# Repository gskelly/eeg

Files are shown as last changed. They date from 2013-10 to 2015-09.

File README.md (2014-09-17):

eeg
===

Software, firmware, and CAD files for Brainboard, a mobile EEG project.
Brainboard interfaces with a custom MATLAB program, BCI2VR
(http://www.engineering.vcu.edu/eegbci/bci2vr_index.html), via Bluetooth.
The core hardware components are the ADS1299 EEG front-end from Texas
Instruments, the AT32UC3L064 microcontroller from Atmel, the MPU-6050 
6-axis inertial measurement unit from InvenSense, and the RN-42 Bluetooth
2.1 module from Microchip/Roving Networks.

Current firmware is for the Atmel AT32UC3L064, a 32-bit AVR microcontroller.
Some experimentation was done with on-line digital processing of the acquired
EEG signals from within the AVR firmware, but this is currently incomplete.
The microcontroller acts as a dumb pipe shuttling 8 channels of 24-bit data
from the ADS1299 and 6 channels of 16-bit data from the MPU-6050, where they
are displayed using the BCI2VR MATLAB GUI. Firmware is flashed to the MCU using
a 10-pin JTAG connection and the AVR Dragon (or other AVR32-compatible
programmer). Code was developed using the free Atmel Studio IDE.

The project predates my use of a proper versioning system, and thus
the hardware folder contains designs (some old, some WIP) for the Brainboard. 
***The most recent complete version is brainboard_wearable_v2.***
Older versions may be viewed for completeness's sake and/or compared with the
thesis document for a full picture of the design process.
The folders "muscleboard" and "brainboard_v2" are works in progress. The former
is meant for single-channel EMG acquisition and acceleration measurements in a
small, 3-electrode form factor that can be mounted on a disposable electrode pad.
This will probably ultimately be moved to its own repository. Brainboard v2 is a
BeagleBone Black cape that takes the BBB support from earlier versions of the
Brainboard and re-implements it in a more elegant fashion (see thesis for details).

**To use the BCI2VR GUI (assumes you already have MATLAB r2011b or later):**

1. Go to the link above and download the required MATLAB files for the basic BCI2VR functionality.

2. Copy btv_brainBoardBtFun.m into the functions folder.

3. Copy brainBoardBt_btv_daq_settings.m and brainBoardBt_14Ch.loc into the setup_files folder.

4. Make sure the toolbox is added to your path. Run bci2vr.m and click "Data Acquisition." 

5. Click the "Load setup file" icon and load brainBoardBt_btv_daq_settings.

6. The program will attempt to open a Bluetooth connection with BrainBoard. It occasionally fails; in this case simply close the GUI and try again.

7. Click the "Play" icon to begin recording.

For more info, check Dr. Ou Bai's documentation for BCI2VR, included with the toolbox.

Questions may be directed toward Graham Kelly, preferably at kellygs@vcu.edu, or at graham.smith.kelly@gmail.com as a backup. Dr. Bai may be reached at obai@vcu.edu.

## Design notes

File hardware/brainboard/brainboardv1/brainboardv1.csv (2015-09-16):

1nF | 1 | C2 | ~
2.2nF | 1 | C53 | ~
4.7nF | 11 | C20 C21 C22 C23 C24 C25 C26 C27 C28 C55 C56 | ~
0.01uF | 3 | C42 C47 C54 | ~
0.1uF | 14 | C1 C6 C11 C12 C15 C16 C17 C18 C29 C31 C33 C34 C35 C50 | ~
0.1uF | 1 | C19 | ~
0.1uF | 3 | C45 C51 C52 | ~
1uF | 7 | C4 C5 C7 C9 C10 C13 C14 | ~
1uF | 5 | C37 C38 C40 C41 C46 | ~
2.2uF | 1 | C30 | ~
2.2uF | 2 | C44 C49 | ~
10uF | 2 | C3 C32 | ~
10uF | 4 | C36 C39 C43 C48 | ~
100uF | 1 | C8 | ~
STAT | 1 | D1 | ~
CONN | 1 | D2 | ~
WP | 1 | P1 | ~
CONN_14 | 1 | P2 | ~
CONN_5X2 | 1 | P3 | ~
BTRST | 1 | P4 | ~
GND | 1 | P5 | ~
-3V3 | 1 | P6 | ~
3V3 | 1 | P7 | ~
+2V5 | 1 | P8 | ~
-2V5 | 1 | P9 | ~
CONN_2X2 | 1 | P10 | ~
330 | 2 | R24 R25 | ~
4.7K | 3 | R1 R2 R3 | ~
4.99K | 13 | R11 R12 R13 R14 R15 R16 R17 R18 R19 R20 R21 R22 R23 | ~
5.6K | 2 | R5 R6 | ~
10K | 1 | R4 | ~
10K | 3 | R7 R8 R26 | ~
499K | 0.1% | 1 | R9 | ~
SMT_BUTTON | 1 | S2
NO BIAS FILT | 1 | SJ3 | SparkFun-Passives-SJ_2S-NO
A2 | 1 | SJ4 | SparkFun-Passives-SJ_2S-NOTRACE
A1 | 1 | SJ5 | SparkFun-Passives-SJ_2S-NOTRACE
CLKSEL | 1 | SJ8 | SparkFun-Passives-SJ_3_PASTE1&2
REF-SRB2 | 1 | SJ1 | SparkFun-Passives-SJ_3_PASTE2&3
DAISY_CS | 2 | SJ2 SJ7 | SparkFun-Passives-SJ_3_PASTE2&3
DAISY_OUT | 1 | SJ6 | SparkFun-Passives-SJ_3_PASTE2&3
I2C Address Select (2&3NC) | 1 | SJ9 | SparkFun-Passives-SJ_3_PASTE2&3
24C256 | 1 | U1
BEAGLEBONE_BLACK | 1 | U2
ATUC3L064 | 1 | U8
BLUETOOTH-RN42 | 1 | U9
MPU6050 | 1 | U13
OPA2376 | 1 | U3 | MSOP8
ADS1299 | 1 | U4 | TQFP_64
TPD4E001DBV | 3 | U5 U6 U7 | ~
TPS60403 | 1 | U10 | ~
TPS73225 | 1 | U11 | ~
TPS72325 | 1 | U12 | ~

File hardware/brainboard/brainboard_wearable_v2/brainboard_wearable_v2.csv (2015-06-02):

1nF | 1 | C7
2.2nF | 1 | C3
4.7nF | 11 | C53 C54 C55 C56 C57 C58 C59 C60 C61 C62 C63
0.01uF | 4 | C4 C33 C34 C35
0.1uF | 5 | C1 C2 C24 C31 C42
0.1uF | 15 | C5 C6 C11 C15 C18 C19 C22 C23 C43 C45 C47 C48 C49 C50 C51
0.1uF | 1 | C52
1uF | 8 | C9 C10 C12 C14 C16 C17 C20 C21
1uF | 4 | C27 C28 C30 C32
2.2uF | 4 | C25 C39 C40 C41
2.2uF | 1 | C44
10uF | 2 | C8 C46
10uF | 5 | C26 C29 C36 C37 C38
100uF | 1 | C13
USB | 1 | CON1
SMAJ7.0A | 1 | D1
BATTLO | 1 | D2
PGOOD | 1 | D3
CHARGE | 1 | D4
STAT | 1 | D5
CONN | 1 | D6
PTC 500mA | 1 | F1
MHOLE | 3 | MTG1 MTG2 MTG3
JST | 1 | P1
CONN_5X2 | 1 | P8
CONN_14 | 1 | P10
1.18k | 1 | R13
2.2k | 4 | R11 R14 R15 R16
2.2k | 2 | R17 R18
4.7k | 2 | R4 R5
4.99K | 12 | R21 R22 R23 R24 R25 R26 R27 R28 R29 R30 R31 R32
10K | 2 | R1 R2
10k | 4 | R6 R7 R19 R20
51.1k | 1 | R9
52.3k | 1 | R12
383k | 1 | R10
499K 0.10% | 1 | R3
562k | 1 | R8
DPDT | 1 | S1
NO BIAS FILT | 1 | SJ1
NTC 10K | 1 | TH1
GND | 2 | TP1 TP2
PREREG | 1 | TP3
-3V3 | 1 | TP4
+2V5 | 1 | TP5
-2V5 | 1 | TP6
BTRST | 1 | TP7
3V3 | 1 | TP8
MPU6050 | 1 | U1
LTC1998 | 1 | U4
BQ24074(T) | 1 | U5
ATUC3L064 | 1 | U10
BLUETOOTH-RN42 | 1 | U11
OPA2376 | 1 | U2
ADS1299 | 1 | U3
TPS60403 | 1 | U6
TPS73233 | 1 | U7
TPS73225 | 1 | U8
TPS72325 | 1 | U9
TPD4E001DBV | 3 | U12 U13 U14

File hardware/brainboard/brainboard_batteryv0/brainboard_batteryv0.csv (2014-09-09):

0.01uF | 2 | C6 C8 | ~
0.1uF | 2 | C1 C11 | ~
0.47uF | 1 | C9 | ~
2.2uF | 1 | C10 | ~
10uF | 5 | C2 C3 C4 C5 C7 | ~
USB-MINI-B | 1 | CON1 | ~
SMAJ7.0A | 1 | D1 | ~
PGOOD | 1 | D2 | ~
CHARGE | 1 | D3 | ~
PMEG2005AEA | 1 | D4 | ~
POWER | 1 | D5 | ~
ALRT | 1 | D6 | ~
PTC 1.95A | 2 | F1 F2 | ~
JST | 1 | P1 | ~
VBAT | 1 | P2 | ~
GND | 1 | P3 | ~
BBB_PMIC | 1 | P4 | ~
VBUS | 1 | P6 | ~
WP | 1 | P7 | ~
EN | 1 | P8 | ~
PREREG | 1 | P9 | ~
3V3 | 1 | P10 | ~
SI2312 | 1 | Q1 | ~
1.18k | 1 | R7 | ~
2.2k | 5 | R8 R10 R11 R18 R19 | ~
4.7k | 3 | R2 R3 R4 | ~
5.6k | 2 | R12 R13 | ~
10k | 1 | R9 | ~
30.1k | 1 | R14 | ~
52.3k | 2 | R15 R16 | ~
75k | 1 | R1 | ~
191k | 1 | R6 | ~
806k | 2 | R5 R17 | ~
SYSOFF | 1 | S1 | ~
BBB_SLEEP | 1 | S2 | ~
TS PMIC | 1 | SJ3 | SparkFun-Passives-SJ_2S
BAT | 2 | SJ1 SJ2 | SparkFun-Passives-SJ_2S-NO
A2-0 | 1 | SJ4 | SparkFun-Passives-SJ_2S-NO
A1-0 | 1 | SJ5 | SparkFun-Passives-SJ_2S-NO
SENSE | 1 | SJ7 | SparkFun-Passives-SJ_2S-NO
LOWBAT_DIS | 1 | SJ6 | SparkFun-Passives-SJ_3_PASTE1&2
NTC 10K | 1 | TH1 | ~
MAX17048 | 1 | U1
BQ24074(T) | 1 | U2
24C256 | 1 | U3 | ~
TPS73601-SON | 1 | U4 | ~
LTC2951-1 | 1 | U5 | ~
BEAGLEBONE_BLACK | 1 | U6 | ~

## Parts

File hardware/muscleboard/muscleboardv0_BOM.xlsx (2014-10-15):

Item Value | Count | Reference | Manufacturer | Distributor | PN | Description | Note
1.5nF | 1 | C19 |  | Digi-Key | 04025C152JAT2A | CAP CER 1500PF 50V 5% X7R 0402
4.7nF | 2 | C13 C14 |  | Digi-Key | CL05B472KB5NNNC | CAP CER 4700PF 50V 10% X7R 0402
0.01uF | 1 | C10 |  | Digi-Key | C0402C103K4RACTU | CAP CER 10000PF 16V 10% X7R 0402 | Need to order
0.1uF | 10 | C1 C2 C3 C5 C15 C20 C21 C9 C23 C25 |  | Digi-Key | CL05A104MP5NNNC | CAP CER 0.1UF 10V 20% X5R 0402
1uF | 4 | C17 C18 C22 C24 |  | Digi-Key | JMK105BJ105KV-F | CAP CER 1UF 6.3V 10% X5R 0402
2.2uF | 1 | C12 |  | Digi-Key | C0402C225M9PACTU | CAP CER 2.2UF 6.3V 20% X5R 0402 | Need to order
4.7uF | 2 | C4 C8 |  | Digi-Key | GRM155R60J475ME47D | CAP CER 4.7UF 6.3V 20% X5R 0402 | Need to order
10uF | 2 | C11 C16 |  | Digi-Key | CL10A106MQ8NNNC | CAP CER 10UF 6.3V 20% X5R 0603
CHG | 1 | D1 |  | Digi-Key | APT1608SGC | LED 1.6X0.8MM 568NM GRN CLR SMD
SCHOTTKY | 1 | D2 |  | Digi-Key | VS-10BQ015-M3/5BT | DIODE SCHOTTKY 15V 1A SMB
RED | 1 | D3 |  | Digi-Key | APT1608SRCPRV | LED 1.6X0.8MM 640NM RED CLR SMD
BLM18PG121SN1 | 1 | FB1 |  | Digi-Key | BLM18PG121SN1D | FERRITE CHIP 120 OHM 2000MA 0603
10uH | 1 | L1 |  | Digi-Key | MLZ1608E100M | INDUCTOR MULTILAYER 10UH 0603
BATT | 1 | P1 |  | Digi-Key | S2B-PH-SM4-TB(LF)(SN) | CONN HEADER PH SIDE 2POS 2MM SMD
USB | 1 | P2 |  | Digi-Key | 690-005-299-043 | CONN MINI USB RCPT RA TYPE B SMD
ICSP | 1 | P3 |  | Digi-Key | 67996-206HLF | CONN HEADER 6POS .100 STR 15AU
2.2k | 2 | R4 R7 |  | Digi-Key | RMCF0402FT2K20 | RES 2.2K OHM 1/16W 1% 0402
10k | 4 | R3 R5 R9 R10 |  | Digi-Key | RMCF0402JT10K0 | RES 10K OHM 1/16W 5% 0402
51k | 1 | R8 |  | Digi-Key | RMCF0402FT51K0 | RES 51K OHM 1/16W 1% 0402
1M | 2 | R2 R12 |  | Digi-Key | RMCF0402JT1M00 | RES 1M OHM 1/16W 5% 0402
2.2M | 1 | R1 |  | Digi-Key | RC1005F225CS | RES 2.2M OHM 1/16W 1% 0402
CHG/ON | 1 | S2 |  | Digi-Key | JS102011SAQN | SWITCH SLIDE 1PDT 6VDC 0.3A SMT
ADS1291 | 1 | U5 |  | Digi-Key | ADS1291IRSMT | IC AFE 24BIT 8KSPS 1CH 32VQFN | Need to order
ATMEGA328P | 1 | U1 |  | Digi-Key | ATMEGA328P-MUR | IC MCU 8BIT 32KB FLASH 32QFN | Need to order
MCP73831T-DFN | 1 | U2 |  | Mouser | MCP73831T-2ACI/MC | Battery Management Charge mgnt contr | Need to order
TPS73233 | 1 | U3 |  | Digi-Key | TPS73233DBVT | IC REG LDO 3.3V 0.25A SOT23-5
BLUETOOTH-RN42 | 1 | U4 |  | Digi-Key | RN42-I/RM | MODULE BLUETOOTH V2.1+EDR | Need to order
ADXL362 | 1 | U6 |  | Digi-Key | ADXL362BCCZ-RL7 | IC ACCEL DIG LO PWR 3AX 16LGA | Need to order
RESONATOR | 1 | Y1 |  | Digi-Key | CSTCE8M00G52-R0 | CER RESONATOR

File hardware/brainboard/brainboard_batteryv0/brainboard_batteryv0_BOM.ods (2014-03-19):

VALUE | REF | COUNT | DESCRIPTION/COMMENTS | VENDOR | PN
0.01uF | C6 C8 | 2 | SM0603 | DigiKey | 1276-1926-1-ND
0.1uF | C1 | 1 | SM0603 | DigiKey | 1276-1258-1-ND
0.47uF | C9 | 1 | SM0603 | DigiKey | 1276-2378-1-ND
2.2uF | C10 | 1 | SM0603 | DigiKey | 1276-1040-1-ND
10uF | C2 C3 C7 | 3 | SM0805 | DigiKey | 1276-2893-1-ND
10uF | C4 C5 | 2 | SM1206 | DigiKey | 1276-2876-1-ND
USB-MINI-B | CON1 | 1 | SMD W/ BOARD GUIDE | DigiKey | 151-1206-1-ND
SMAJ7.0A | D1 | 1 | ZENER | DigiKey | SMAJ7.0ALFCT-ND
PGOOD | D2 | 1 | LED | DigiKey | -
CHARGE | D3 | 1 | LED | DigiKey | -
PMEG2005AEA | D4 | 1 | SCHOTTKY | DigiKey | 568-6498-1-ND
PTC 1.95A | F1 F2 | 2 | LITTELFUSE 1812L | DigiKey | F3485CT-ND
JST | P1 | 1 | JST FEM PH 2PIN SMD | DigiKey | 455-1749-1-ND
VBAT | P2 | 1 | TP | - | -
GND | P3 | 1 | TP | - | -
BBB_PMIC | P4 | 1 | 2X2 MALE
~ALRT | P5 | 1 | TP | - | -
VBUS | P6 | 1 | TP | - | -
WP | P7 | 1 | TP | - | -
EN | P8 | 1 | TP | - | -
PREREG | P9 | 1 | TP | - | -
3V3 | P10 | 1 | TP | - | -
SI2312 | Q1 | 1 | NMOS | DigiKey | SI2312CDS-T1-GE3CT-ND
1.18k | R7 | 1 | 1% | DigiKey | 311-1.18KHRCT-ND
1.5k | R10 R11 | 2 |  | DigiKey | 311-1.5KGRCT-ND
2.2k | R8 | 1 | 1% | DigiKey | 311-2.20KHRCT-ND
4.7k | R2 R3 R4 | 3 |  | DigiKey | 311-4.7KGRCT-ND
5.6k | R12 R13 | 2 |  | DigiKey | 311-5.6KGRCT-ND
10k | R9 | 1 |  | DigiKey | 311-10KGRCT-ND
30.1k | R14 | 1 | 1% | DigiKey | 311-30.1KHRCT-ND
52.3k | R15 R16 | 2 | 1% | DigiKey | 311-52.3KHRCT-ND
75k | R1 | 1 | 1% | DigiKey | 311-75.0KHRCT-ND
191k | R6 | 1 | 1% | DigiKey | 311-191KHRCT-ND
806k | R5 R17 | 2 | 1% | DigiKey | 311-806KHRCT-ND
SYSOFF | S1 | 1 | MOM BUTTON | DigiKey | -
BBB_SLEEP | S2 | 1 | MOM BUTTON | DigiKey | -
TO PMIC | SJ3 | 1 | SOLDER JUMPER | - | -
BAT | SJ1 SJ2 | 2 | SOLDER JUMPER | - | -
A2-0 | SJ4 | 1 | SOLDER JUMPER | - | -
A1-0 | SJ5 | 1 | SOLDER JUMPER | - | -
LOWBAT_DIS | SJ6 | 1 | SOLDER JUMPER | - | -
NTC 10K | TH1 | 1 | SM0402 | DigiKey | BC2329CT-ND
MAX17048 | U1 | 1 | FUEL GAUGE | Mouser | 700-MAX17048G+
BQ24074(T) | U2 | 1 | CHARGER | DigiKey | 296-23798-1-ND
24C256 | U3 | 1 | EEPROM | DigiKey | -
TPS73601-SON | U4 | 1 | LDO | DigiKey | 296-27062-1-ND
LTC2951-1 | U5 | 1 | ON/OFF CTRL IC | DigiKey | LTC2951CDDB-1#TRMPBFCT-ND
BEAGLEBONE_BLACK | U6 | 1 | CAPE FOOTPRINT | - | -

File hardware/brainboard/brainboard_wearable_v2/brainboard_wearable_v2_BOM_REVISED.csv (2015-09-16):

VALUE | COUNT | REF
1nF | 1 | C7 | ~ | Kemet | C0603C102K3RACTU | DigiKey | $0.10/1 $0.02/10 $0.0108/50
2.2nF | 1 | C3 | ~
4.7nF | 11 | C53 C54 C55 C56 C57 C58 C59 C60 C61 C62 C63 | ~ | Kemet | C0603C472K5RACTU | DigiKey | $0.10/1 $0.03/10 $0.0162/50
0.01uF | 4 | C4 C33 C34 C35 | ~
0.1uF | 5 | C1 C2 C24 C31 C42 | ~
0.1uF | 15 | C5 C6 C11 C15 C18 C19 C22 C23 C43 C45 C47 C48 C49 C50 C51 | ~ | Kemet | C0603C104K4RACTU | DigiKey | $0.10/1 $0.022/10 $0.0118/50
0.1uF | 1 | C52 | ~ | Kemet | C0603C104K4RACTU | DigiKey | $0.10/1 | $0.022/10 | $0.0118/50
1uF | 8 | C9 C10 C12 C14 C16 C17 C20 C21 | ~ | Kemet | C0603C105K8PACTU | DigiKey | $0.10/1 $0.039/10 $0.021/50
1uF | 4 | C27 C28 C30 C32 | ~
2.2uF | 4 | C25 C39 C40 C41 | ~
2.2uF | 1 | C44 | ~ | Kemet | C0603C225K8PACTU | DigiKey | $0.17/1 $0.113/10 $0.0676/50
10uF | 2 | C8 C46 | ~ | Kemet | C0805C106Z8VACTU | DigiKey | $0.16/1 $0.111/10 $0.063/50
10uF | 5 | C26 C29 C36 C37 C38 | ~
100uF | 1 | C13 | ~ | Vishay Sprague | TL8A0107M010C | DigiKey | $1.35/1 $1.128/10
USB | 1 | CON1 | ~
SMAJ7.0A | 1 | D1 | ~
BATTLO | 1 | D2 | ~
PGOOD | 1 | D3 | ~
CHARGE | 1 | D4 | ~
STAT | 1 | D5 | ~ | Kingbright Company LLC | APT1608SRCPRV | DigiKey | $0.17/1 $0.131/10 $0.1044/25
CONN | 1 | D6 | ~ | Kingbright Company LLC | APT1608SGC | DigiKey | $0.16/1 $0.117/10 $0.0936/25
PTC 500mA | 1 | F1 | ~
MHOLE | 3 | MTG1 MTG2 MTG3 | ~
JST | 1 | P1 | ~
CONN_5X2 | 1 | P8 | ~ | FCI | 95278-101B10LF | Mouser | $0.86/1 $0.737/10 $0.673/100
CONN_14 | 1 | P10 | ~
1.18k | 1 | R13 | ~
2.2k | 4 | R11 R14 R15 R16 | ~
2.2k | 2 | R17 R18 | ~ | Stackpole Electronics | RMCF0603JT330R | DigiKey | $0.02/1 $0.017/10 $0.0092/50
4.7k | 2 | R4 R5 | ~
4.99K | 12 | R21 R22 R23 R24 R25 R26 R27 R28 R29 R30 R31 R32 | ~ | Stackpole Electronics | RNCS0603BKE4K99 | DigiKey | $0.70/1 $0.475/10 $0.2876/50
10K | 2 | R1 R2 | ~ | Stackpole Electronics | RMCF0603JT10K0 | DigiKey | $0.02/1 $0.017/10 $0.0092/50
10k | 4 | R6 R7 R19 R20 | ~
51.1k | 1 | R9 | ~
52.3k | 1 | R12 | ~
383k | 1 | R10 | ~
499K 0.10% | 1 | R3 | ~ | Stackpole Electronics | RNCS0805BKE499K | DigiKey | $0.77/1 | $0.523/10 | $0.3162/50
562k | 1 | R8 | ~
DPDT | 1 | S1 | ~
NO BIAS FILT | 1 | SJ1 | SparkFun-Passives-SJ_2S-NO
NTC 10K | 1 | TH1 | ~
GND | 2 | TP1 TP2 | ~
PREREG | 1 | TP3 | ~
-3V3 | 1 | TP4 | ~
+2V5 | 1 | TP5 | ~
-2V5 | 1 | TP6 | ~
BTRST | 1 | TP7 | ~
3V3 | 1 | TP8 | ~
MPU6050 | 1 | U1
LTC1998 | 1 | U4
BQ24074(T) | 1 | U5
ATUC3L064 | 1 | U10 |  | Atmel | AT32UC3L064-AUT | DigiKey | $7.80/1 $4.898/25
BLUETOOTH-RN42 | 1 | U11 |  | Microchip Technology | RN42-I/RM | DigiKey | $19.14/1 $15.95/10
OPA2376 | 1 | U2 | MSOP8 | Texas Instruments | OPA2376AIDGKR | DigiKey | $2.73/1 $2.462/10 $2.206/25
ADS1299 | 1 | U3 | TQFP_64 | Texas Instruments | ADS1299IPAG | DigiKey | $58.14/1
TPS60403 | 1 | U6 | ~
TPS73233 | 1 | U7 | ~
TPS73225 | 1 | U8 | ~
TPS72325 | 1 | U9 | ~
TPD4E001DBV | 3 | U12 U13 U14 | ~

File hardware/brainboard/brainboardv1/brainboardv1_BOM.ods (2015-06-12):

VALUE | REF | COUNT | DESCRIPTION/COMMENTS | VENDOR | PN | Price Breaks
1nF | C36 | 1 | Kemet Ceramic | DigiKey | C0603C102K3RACTU | $0.10/1 $0.02/10 $0.0108/50
2.2nF | C53 | 1 | Samsung Electro-Mechanics | DigiKey | CL10A225KO8NNNC
4.7nF | C4 C5 C6 C7 C8 C9 C10 C11 C12 | 9 | Kemet | DigiKey | C0603C472K5RACTU | $0.10/1 $0.03/10 $0.0162/50
0.01uF | C27 C28 C54 | 3 | Kemet | DigiKey | C0603C103K5RACTU
0.1uF | C1 C2 C3 C13 C15 C17 C18 C19 C33 C34 C35 C40 C45 C46 C49 C50 C51 C52 | 18 | Kemet | DigiKey | C0603C104K4RACTU | $0.10/1 $0.022/10 $0.0118/50
1uF | C21 C22 C24 C25 C26 C38 C39 C41 C43 C44 C47 C48 | 12 | Kemet | DigiKey | C0603C105K8PACTU | $0.10/1 $0.039/10 $0.021/50
2.2uF | C14 C31 C32 | 3 | Kemet | DigiKey | C0603C225K8PACTU
10uF | C16 C20 C23 C29 C30 C37 | 6 | Kemet | DigiKey | C0805C106Z8VACTU | $0.16/1 $0.111/10 $0.063/50
100uF | C42 | 1 | Vishay Sprague Tant Pol | DigiKey | TL8A0107M010C | $1.35/1 $1.128/10
RED | D1 | 1 | Kingbright Company LLC | DigiKey | APT1608SRCPRV | $0.17/1 $0.131/10 $0.1044/25
GREEN | D2 | 1 | Kingbright Company LLC | DigiKey | APT1608SGC | $0.16/1 $0.117/10 $0.0936/25
CONN_14 | P2 | 1 | Sullins Connector | DigiKey | PPTC141LGBN-RC
CONN_5X2 | P3 | 1 | FCI | DigiKey | 68602-110HLF | $0.33/1 $0.308/10 $0.2644/25
330 | R20 R21 | 2 | Stackpole Electronics | DigiKey | RMCF0603JT330R | $0.02/1 $0.017/10 $0.0092/50
4.7K | R1 R2 R3 | 3 | Stackpole Electronics | DigiKey | RMCF0603JT4K70 | $0.02/1 $0.017/10 $0.0092/50
4.99K | R7 R8 R9 R10 R11 R12 R13 R14 R15 R16 R17 R18 R19 | 13 | Stackpole Electronics | DigiKey | RNCS0603BKE4K99 | $0.70/1 $0.475/10 $0.2876/50
5.6K | R5 R6 | 2 | Stackpole Electronics | DigiKey | RMCF0603JT5K60 | $0.02/1 $0.017/10 $0.0092/50
10K | R4 | 1 | Stackpole Electronics | DigiKey | RMCF0603JT10K0 | $0.02/1 $0.017/10 $0.0092/50
10K | R22 R23 R24 R26 R27 | 5 | Stackpole Electronics | DigiKey | RMCF0603JT10K0 | $0.02/1 $0.017/10 $0.0092/50
499K 0.10% | R25 | 1 | Stackpole Electronics | DigiKey | RNCS0805BKE499K | $0.77/1 $0.523/10 $0.3162/50
SMT_BUTTON | S2 | 1 | C&K Components | DigiKey | KMR231GLFS | $0.64/1 $0.604/10 $0.5436/25
24C256 | U1 | 1 | Fremont Micro Devices USA | DigiKey | FT24C256A-UMR-B | $0.92/1 $0.805/10 $0.7132/25
BEAGLEBONE_BLACK | U2 | 1
ATUC3L064 | U6 | 1 | Atmel | DigiKey | AT32UC3L064-AUT | $7.80/1 $4.898/25
BLUETOOTH-RN42 | U7 | 1 | Microchip Technology | DigiKey | RN42-I/RM | $19.14/1 $15.95/10
MPU6050 | U13 | 1 | InvenSense | DigiKey | 1428-1007-1-ND
OPA2376 | U11 | 1 | Texas Instruments | DigiKey | OPA2376AIDGKR | $2.73/1 $2.462/10 $2.206/25
ADS1299 | U12 | 1 | Texas Instruments | DigiKey | ADS1299IPAG | $58.14/1
TPD4E001DBV | U3 U4 U5 | 3 | Texas Instruments | DigiKey | 296-28203-1-ND
TPS60403 | U8 | 1 | Texas Instruments | DigiKey | 296-13418-1-ND
TPS73225 | U9 | 1 | Texas Instruments | DigiKey | 296-15810-1-ND
TPS72325 | U10 | 1 | Texas Instruments | DigiKey | 296-15799-1-ND

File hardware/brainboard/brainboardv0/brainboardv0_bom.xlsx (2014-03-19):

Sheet: Order Request Form
Item | Vendor | PN | Count/Bd | Count/Run | Order | Unit Price | Subtotal
RES 330 OHM 1/10W 5% 0603 | DigiKey | RMCF0603JT330R | 2 | 6 | 10 | $0.0170 | $0.17
CAP CER 0.1UF 16V 10% X7R 0603 | DigiKey | C0603C104K4RACTU | 15 | 45 | 50 | $0.0118 | $0.59
CAP TANT 100UF 10V 20% 1206 | DigiKey | TL8A0107M010C | 1 | 3 | 10 | $1.1280 | $11.28
RES 10K OHM 1/10W 5% 0603 | DigiKey | RMCF0603JT10K0 | 5 | 15 | 20 | $0.0170 | $0.34
CAP CER 10UF 10V Y5V 0805 | DigiKey | C0805C106Z8VACTU | 2 | 6 | 20 | $0.1110 | $2.22
CAP CER 1000PF 25V 10% X7R 0603 | DigiKey | C0603C102K3RACTU | 1 | 3 | 10 | $0.0200 | $0.20
CAP CER 1UF 10V 10% X5R 0603 | DigiKey | C0603C105K8PACTU | 7 | 21 | 50 | $0.0210 | $1.05
CAP CER 2.2UF 10V 10% X5R 0603 | DigiKey | C0603C225K8PACTU | 1 | 3 | 10 | $0.1130 | $1.13
CAP CER 4700PF 50V 10% X7R 0603 | DigiKey | C0603C472K5RACTU | 9 | 27 | 50 | $0.0162 | $0.81
RES 4.7K OHM 1/10W 5% 0603 | DigiKey | RMCF0603JT4K70 | 3 | 9 | 20 | $0.0170 | $0.34
RES 4.99K OHM 1/16W 0.1% 0603 | DigiKey | RNCS0603BKE4K99 | 11 | 33 | 50 | $0.2876 | $14.38
RES 5.6K OHM 1/10W 5% 0603 | DigiKey | RMCF0603JT5K60 | 2 | 6 | 20 | $0.0170 | $0.34
RES 499K OHM 1/10W 0.1% 0805 | DigiKey | RNCS0805BKE499K | 1 | 3 | 10 | $0.5230 | $5.23
LED 1.6X0.8MM 568NM GRN CLR SMD | DigiKey | APT1608SGC | 1 | 3 | 10 | $0.1170 | $1.17
LED 1.6X0.8MM 640NM RED CLR SMD | DigiKey | APT1608SRCPRV | 1 | 3 | 10 | $0.1310 | $1.31
SWITCH TACTILE SPST-NO 0.05A 32V | DigiKey | KMR231GLFS | 1 | 3 | 10 | $0.6040 | $6.04
CONN FEMALE 12POS .100" R/A GOLD | DigiKey | PPPC121LGBN-RC | 1 | 3 | 10 | $0.8400 | $8.40
BERGSTIK II .100" DR STRAIGHT | DigiKey | 68602-110HLF | 1 | 3 | 10 | $0.6710 | $6.71
IC EEPROM 256KBIT 1MHZ 8MSOP | DigiKey | FT24C256A-UMR-B | 1 | 3 | 5 | $0.9200 | $4.60
IC AFE 24BIT 16KSPS LN 64TQFP | DigiKey | ADS1299IPAG | 1 | 3 | 3 | $58.1400 | $174.42
IC MCU 32BIT 64KB FLASH 48TQFP | DigiKey | AT32UC3L064-AUT | 1 | 3 | 3 | $7.8000 | $23.40
MODULE BLUETOOTH V2.1+EDR | DigiKey | RN42-I/RM | 1 | 3 | 3 | $19.1400 | $57.42
IC OPAMP GP 5.5MHZ DUAL 8VSSOP | DigiKey | OPA2376AIDGKR | 1 | 3 | 5 | $2.7300 | $13.65
Low-Cap 4Ch +/-15kV ESD Protection Array | Mouser | 595-TPD4E001DBVR | 3 | 9 | 10 | $0.3600 | $3.60
IC REG LDO 5V 0.15A SOT23-5 | DigiKey | TPS73150DBVT | 1 | 3 | 5 | $1.2300 | $6.15
Stacking Header Set for Beagle Bone Capes (2x23) | Adafruit | 706 | 1 | 3 | 3 | $4.9500 | $14.85
 |  | BD/RUN: | 3 |  | PARTS TOTAL/RUN: |  | $359.80
 |  | COST/BD: | $25.00 |  | PARTS TOTAL/BD: |  | $119.93
 |  | BD TOTAL/RUN: | $75.00
 |  |  |  |  | GRAND TOTAL/RUN: |  | $434.80
 |  |  |  |  | GRAND TOTAL/BD: |  | $144.93

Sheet: Price Breaks
Price Break | RMCF0603JT330R | C0603C104K4RACTU | TL8A0107M010C | RMCF0603JT10K0 | C0805C106Z8VACTU | C0603C102K3RACTU | C0603C105K8PACTU | C0603C225K8PACTU | C0603C472K5RACTU | RMCF0603JT4K70 | RNCS0603BKE4K99 | RMCF0603JT5K60 | RNCS0805BKE499K | APT1608SGC | APT1608SRCPRV | KMR231GLFS | PPPC121LGBN-RC | 68602-110HLF | FT24C256A-UMR-B | ADS1299IPAG | AT32UC3L064-AUT | RN42-I/RM | OPA2376AIDGKR | 595-TPD4E001DBVR | TPS73150DBVT | 706
0 | $0.00 | $0.00 | $0.00 | $0.00 | $0.00 | $0.00 | $0.00 | $0.00 | $0.00 | $0.00 | $0.00 | $0.00 | $0.00 | $0.00 | $0.00 | $0.00 | $0.00 | $0.00 | $0.00 | $0.00 | $0.00 | $0.00 | $0.00 | $0.00 | $0.00 | $0.00
1 | $0.020000 | $0.100000 | $1.350000 | $0.020000 | $0.160000 | $0.100000 | $0.100000 | $0.170000 | $0.100000 | $0.020000 | $0.700000 | $0.020000 | $0.770000 | $0.160000 | $0.170000 | $0.640000 | $1.010000 | $0.710000 | $0.920000 | $58.140000 | $7.800000 | $19.140000 | $2.730000 | $0.480000 | $1.230000 | $4.950000
10 | $0.017000 | $0.022000 | $1.128000 | $0.017000 | $0.111000 | $0.020000 | $0.039000 | $0.113000 | $0.030000 | $0.017000 | $0.475000 | $0.017000 | $0.523000 | $0.117000 | $0.131000 | $0.604000 | $0.840000 | $0.671000 | $0.805000 | $54.720000 | $7.800000 | $15.950000 | $2.462000 | $0.360000 | $1.091000 | $4.460000
25 | $0.017000 | $0.022000 | $1.128000 | $0.017000 | $0.111000 | $0.020000 | $0.039000 | $0.113000 | $0.030000 | $0.017000 | $0.475000 | $0.017000 | $0.523000 | $0.117000 | $0.131000 | $0.543600 | $0.777600 | $0.575200 | $0.713200 | $54.720000 | $4.898000 | $15.437600 | $2.206000 | $0.360000 | $0.984800 | $4.460000
50 | $0.009200 | $0.011800 | $1.128000 | $0.009200 | $0.063000 | $0.010800 | $0.021000 | $0.067600 | $0.016200 | $0.009200 | $0.287600 | $0.009200 | $0.316200 | $0.093600 | $0.104400 | $0.483200 | $0.699800 | $0.488800 | $0.621000 | $54.720000 | $4.898000 | $15.437600 | $2.206000 | $0.360000 | $0.984800 | $4.460000
100 | $0.007000 | $0.009900 | $0.828000 | $0.007000 | $0.052200 | $0.008800 | $0.017200 | $0.057000 | $0.013800 | $0.007000 | $0.237500 | $0.007000 | $0.261300 | $0.084500 | $0.094300 | $0.463000 | $0.622000 | $0.488800 | $0.540520 | $46.170000 | $4.353600 | $15.437600 | $1.154300 | $0.190000 | $0.461700 | $3.960000
250 | $0.005200 | $0.008120 | $0.720000 | $0.005200 | $0.043200 | $0.007400 | $0.014360 | $0.046520 | $0.011240 | $0.005200 | $0.187520 | $0.005200 | $0.206240 | $0.078000 | $0.087000 | $0.422720 | $0.544240 | $0.488800 | $0.460000 | $45.315000 | $4.353600 | $15.437600 | $1.132880 | $0.190000 | $0.461700 | $3.960000
500 | $0.003840 | $0.006940 | $0.672000 | $0.003840 | $0.036600 | $0.006300 | $0.012260 | $0.039000 | $0.009620 | $0.003840 | $0.160000 | $0.003840 | $0.176000 | $0.070200 | $0.078300 | $0.402600 | $0.497600 | $0.488800 | $0.402510 | $44.460000 | $4.353600 | $15.437600 | $1.111500 | $0.190000 | $0.461700 | $3.960000
750 | $0.003840 | $0.006940 | $0.672000 | $0.003840 | $0.036600 | $0.006300 | $0.012260 | $0.039000 | $0.009620 | $0.003840 | $0.160000 | $0.003840 | $0.176000 | $0.070200 | $0.078300 | $0.402600 | $0.497600 | $0.488800 | $0.402510 | $43.605000 | $4.353600 | $15.437600 | $1.109012 | $0.190000 | $0.461700 | $3.960000
1000 | $0.002560 | $0.005400 | $0.528000 | $0.002560 | $0.036600 | $0.004950 | $0.009630 | $0.034500 | $0.007500 | $0.002560 | $0.160000 | $0.002560 | $0.176000 | $0.070200 | $0.078300 | $0.332150 | $0.450950 | $0.488800 | $0.368000 | $42.750000 | $4.353600 | $15.437600 | $1.109012 | $0.170000 | $0.461700 | $3.960000
2500 | $0.002160 | $0.005400 | $0.528000 | $0.002160 | $0.036600 | $0.004950 | $0.009630 | $0.034500 | $0.007500 | $0.002160 | $0.160000 | $0.002160 | $0.176000 | $0.070200 | $0.078300 | $0.332150 | $0.404300 | $0.488800 | $0.333500 | $42.750000 | $4.353600 | $15.437600 | $1.109012 | $0.170000 | $0.461700 | $3.960000

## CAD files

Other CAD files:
hardware/brainboard/brainboardv0/brainboardv0-F_Paste.dxf

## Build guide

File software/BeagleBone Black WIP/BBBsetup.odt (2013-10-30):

BeagleBone Black

1. Login

User: ubuntu

Password: ubuntu

2. SSH connection

From Terminal on host:

ssh ubuntu@172.22.193.103

The board will request the password before allow you to access it. After the connection is established, the experience is the same as sending commands to a terminal in the board itself.

If the IP changes, you can turn it on, log in using the HDMI cable and type

ifconfig

Look for “inet addr” under “eth0”.

3. UART / SPI Ports

To enable the I/O pins, we have to set their mux to expected functionality:

First, we have to change the permission mode of the slots file:

sudo chmod 666 /sys/devices/bone_capemgr.*/slots

You'll have to type the user's password.

Then, you add the slots you want:

echo enable-uart5 > /sys/devices/bone_capemgr.*/slots

echo BB-SPI1-01 > /sys/devices/bone_capemgr.*/slots

(For more information on how these files were generated, check my notes on days 06/07 and 06/11 and Google for Hipster Circuits UART or Hipster Circuits SPI).

For USART, you have to allow the file to be written and read:

sudo chmod 666 /dev/ttyO4

Shortcut:

In the BeagleBone Black, there is a file that has all this commands. If you type

sudo cat pin/pins.txt

it will be displayed in the screen and you can copy-and-paste with Crtl+Shift+C and Ctrl+Shift+V (when using SSH connection). The “Check” section allows you to check if the files were actually created.

4. Qt

Qt also needs some files to allow it to interact with them, such as the framebuffer device and mouse/keyboard drivers.

sudo chmod 666 /dev/tty0 /dev/fb0 /dev/input/event*

This line is under qtchmod.txt, in home directory for user ubuntu.

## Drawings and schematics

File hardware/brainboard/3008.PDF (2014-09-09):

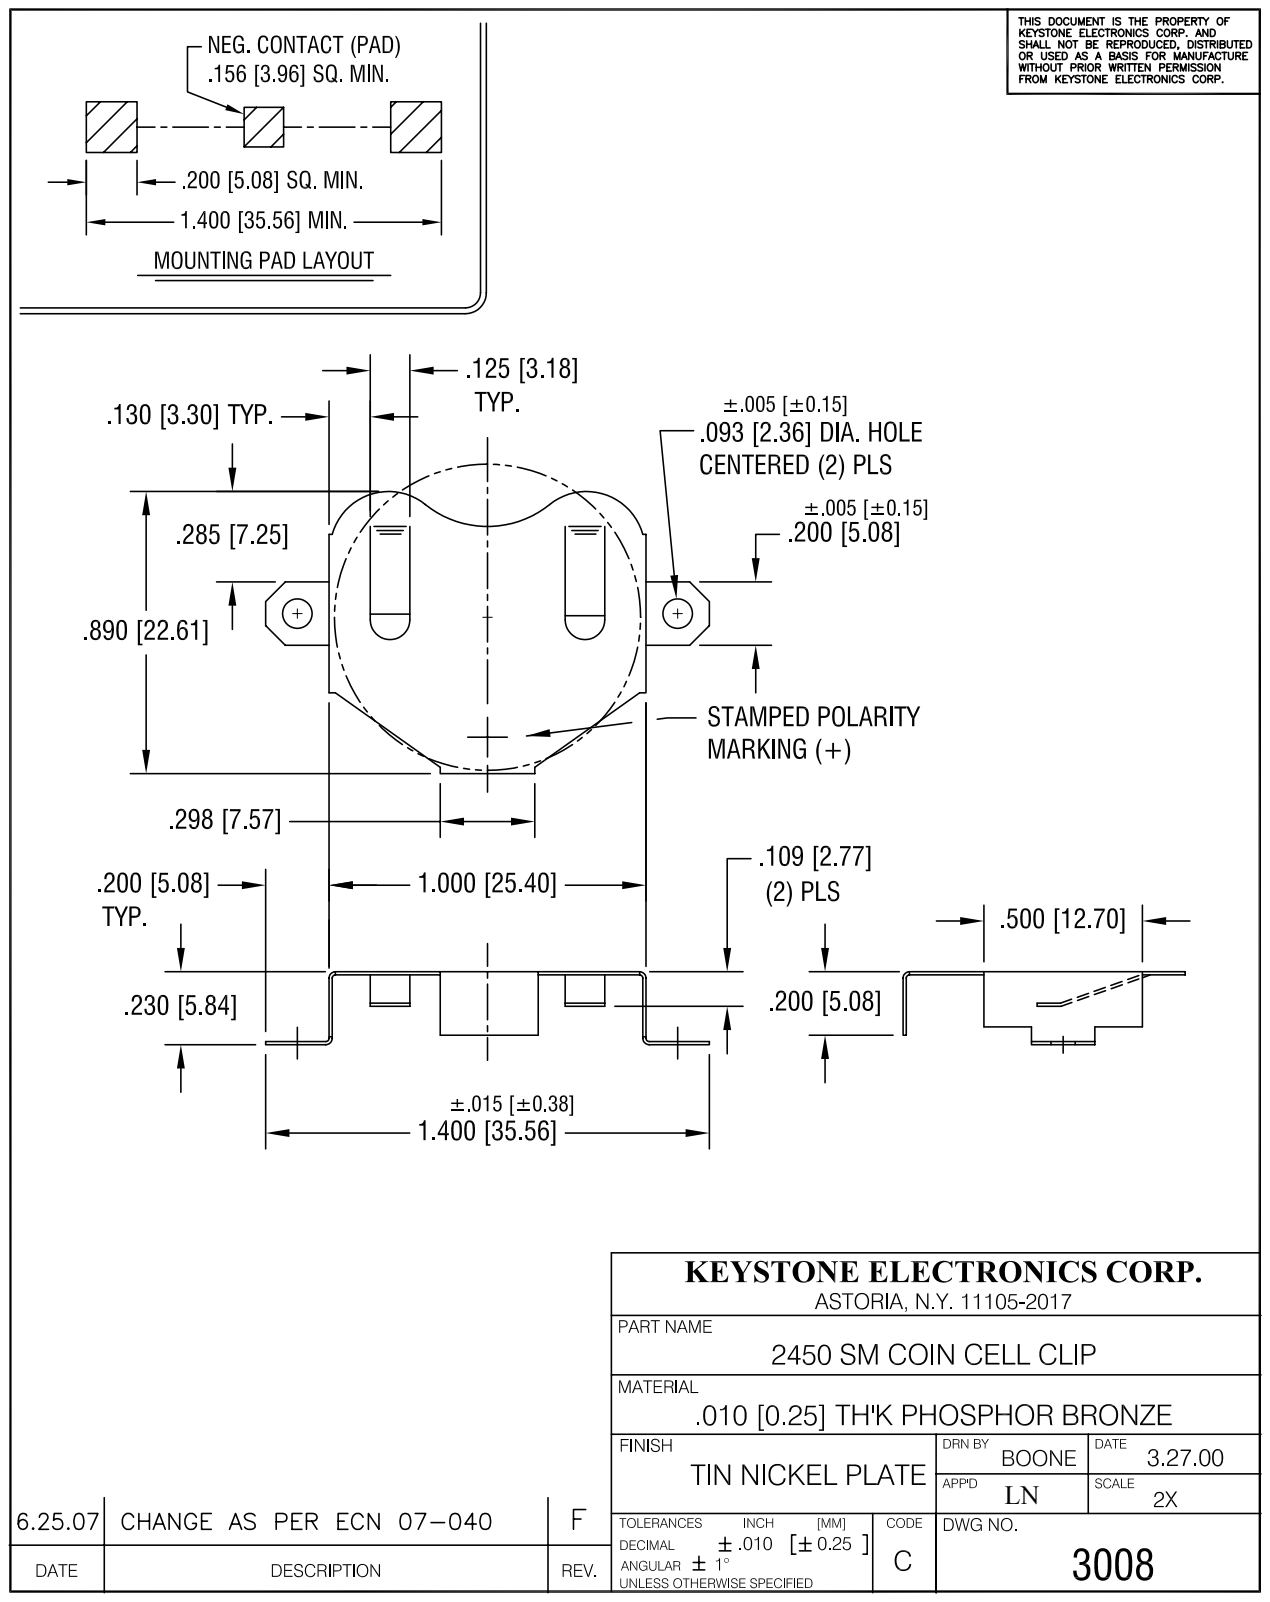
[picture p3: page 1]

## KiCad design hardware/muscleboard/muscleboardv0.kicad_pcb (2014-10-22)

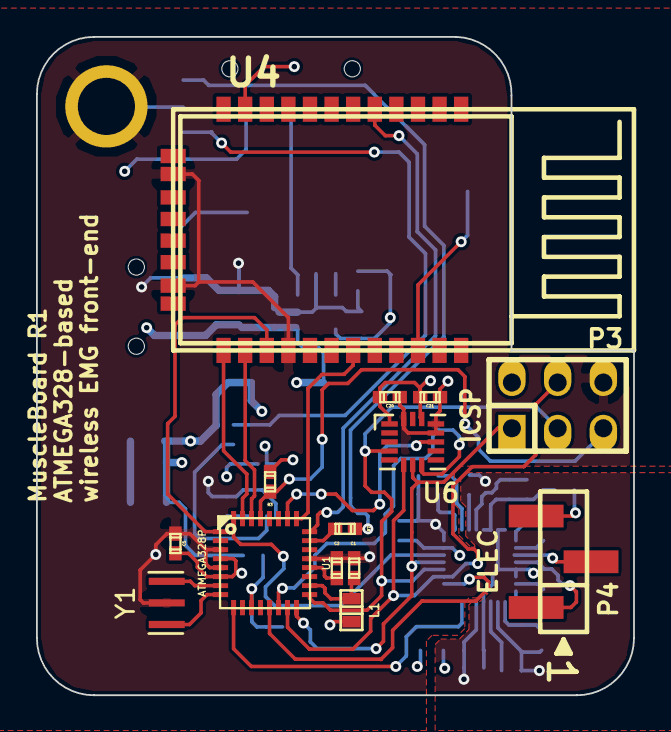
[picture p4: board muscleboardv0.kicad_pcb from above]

Board: 4 copper layers, 33.2 x 36.6 mm, 54 parts (0 on the bottom side), 47 nets.

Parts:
C1, C2, C3, C5, C9, C15, C20, C21, C23, C25: 0.1uF; c_0402
C4, C8: 4.7uF; c_0805
C10: 0.01uF; c_0402
C11, C16: 10uF; c_0603
C12: 2.2uF; c_0402
C13, C14: 4.7nF; c_0402
C17, C18, C22, C24: 1uF; c_0402
C19: 1.5nF; c_0402
D1: CHG; Led_0603
D2: LSM115JE3/TR13; do214aa
D3: RED; Led_0603
FB1: BLM18PG121SN1; inductor_smd_0603
L1: 10uH; inductor_smd_0603
MTG1: MHOLE; BBB_MHOLE
P1: BATT; s2b-ph-sm4-tb
P2: USB; USB_MINI_B
P3: ICSP; pin_strip_3x2
P4: ELEC; bb02-hy03a
R1: 2.2M; r_0402
R2, R12: 1M; r_0402
R3, R5, R9, R10: 10k; r_0402
R4, R7: 2.2k; r_0402
R8: 51k; r_0402
S2: CHG/ON; JS102011SAQN
TP1: GND; testpoint_1mm5
TP2: 3V3; testpoint_1mm5
TP3: FACT; testpoint_1mm5
U1: ATMEGA328P; pvqfn-n32-nopad
U2: MCP73831T-DFN; dfn8-2x3
U3: TPS73233; sot23-5
U4: BLUETOOTH-RN42; roving_rn-42
U5: ADS1291; s-pvqfn-n32-nopad
U6: ADXL362; 16-LGA-3x3.25
Y1: RESONATOR; smd_resonator_1206

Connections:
+3.3V: C5.1, C11.1, C12.1, C20.1, C21.1, C24.1, C25.1, FB1.1, L1.2, P3.2, R3.1, TP2.1, U1.4, U1.6, U3.5, U4.11, U5.23, U6.1, U6.14
+BATT: C4.1, D2.1, P1.1, R1.1, U2.3, U2.4
/AREF: C2.1, U1.20
/AVCC: C1.1, L1.1, U1.18
/Analog front-end/GPIO1: R9.1, U5.26
/Analog front-end/GPIO2: R10.1, U5.25
/Analog front-end/PGA1N: C13.2, U5.1
/Analog front-end/PGA1P: C13.1, U5.2
/Analog front-end/PGA2N: C14.2, U5.7
/Analog front-end/PGA2P: C14.1, U5.8
/Analog front-end/RLDIN: C19.1, R8.1, R12.1, U5.29, U5.30
/Analog front-end/RLDINV: C19.2, R12.2, U5.28
/Analog front-end/VCAP1: C18.1, U5.11
/Analog front-end/VCAP2: C17.1, U5.27
/Analog front-end/VREFP: C15.1, C16.1, U5.9
/BATT_MON: C3.1, R1.2, R2.1, U1.11
/BT_CONN: U1.25, U4.19
/BT_RESET: U1.24, U4.5
/FACTORY_RESET: TP3.1, U4.22
/MCU_RX: U1.30, U4.14
/MCU_TX: U1.31, U4.13
/USER_LED: R7.2, U1.23
/~MCU_CTS: U1.1, U4.15
CH1N: P4.2, U5.3
CH1P: P4.1, U5.4
GND: C1.2, C2.2, C3.2, C4.2, C5.2, C8.2, C9.2, C10.2, C11.2, C12.2, C15.2, C16.2, C17.2, C18.2, C20.2, C21.2, C22.2, C23.2, C24.2, C25.2, D3.2, MTG1.1, P1.2, P2.5, P2.6, P2.7, P2.8, P2.9, P3.6, R2.2, R5.2, R9.2, R10.2, S2.3, TP1.1, U1.3, U1.5, U1.21, U2.5, U2.9, U3.2, U4.16, U4.28, U4.29, U5.10, U5.13, U5.24, U6.12, U6.13, U6.16, Y1.2
MISO: P3.1, U1.16, U5.21, U6.7
MOSI: P3.4, U1.15, U5.19, U6.6
unnamed: D3.1, R7.1
unnamed: U1.8, Y1.3
unnamed: U1.7, Y1.1
unnamed: R5.1, U2.8
unnamed: C10.1, U3.4
unnamed: S2.2, U3.3
unnamed: R4.2, U2.6
unnamed: D1.2, R4.1
unnamed: C22.1, C23.1
unnamed: U5.5, U5.6, U5.12, U5.31, U5.32
RLD: P4.3, R8.2
SCLK: P3.3, U1.17, U5.20, U6.4
VBUS: C8.1, C9.1, D1.1, D2.2, P2.1, S2.1, U2.1, U2.2, U3.1
XL_INT1: U1.26, U6.11
~AFE_CS: U1.13, U5.18
~AFE_DRDY: U1.32, U5.22
~AFE_PWDN: U1.9, U5.15
~MCU_RESET: P3.5, R3.2, U1.29
~XL_CS: U1.14, U6.8

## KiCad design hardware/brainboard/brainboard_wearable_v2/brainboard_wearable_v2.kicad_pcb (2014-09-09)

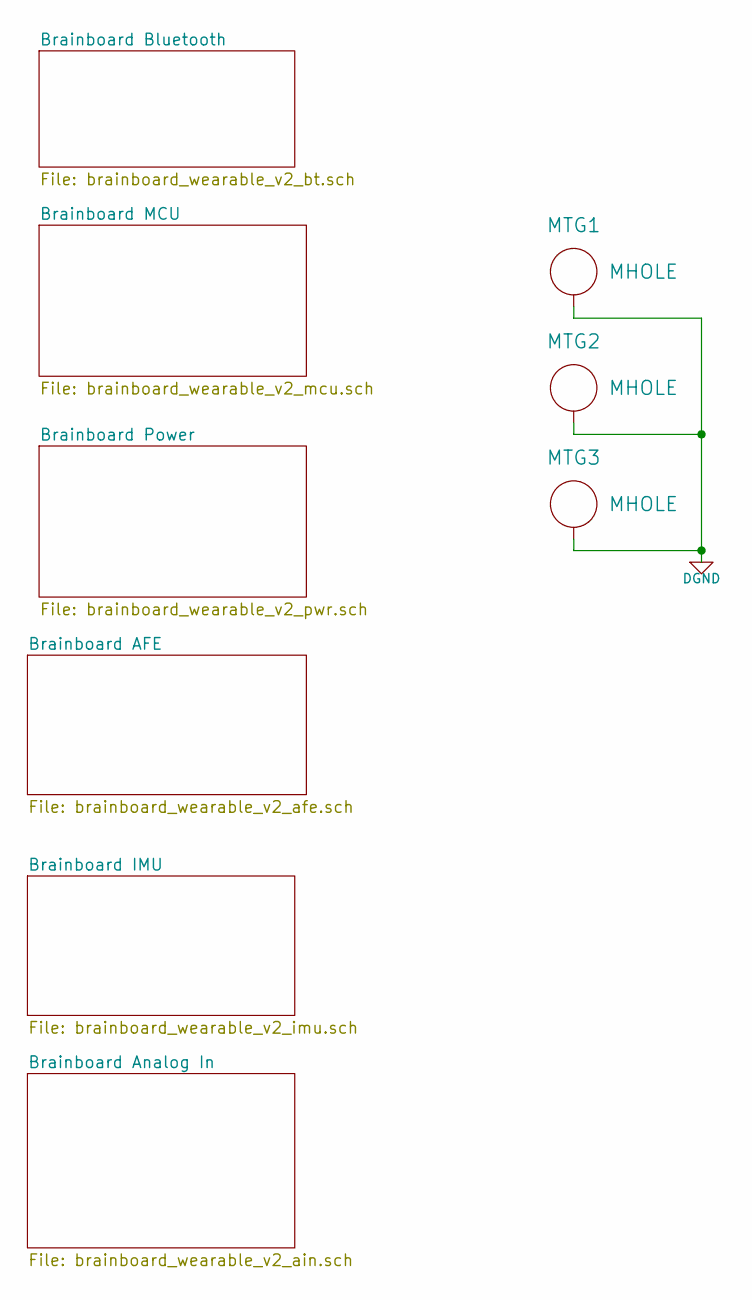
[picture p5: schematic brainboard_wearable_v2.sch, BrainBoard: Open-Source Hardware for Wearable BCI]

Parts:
MTG1, MTG2, MTG3: MHOLE

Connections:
AGND: MTG1.1, MTG2.1, MTG3.1; also elsewhere on the board

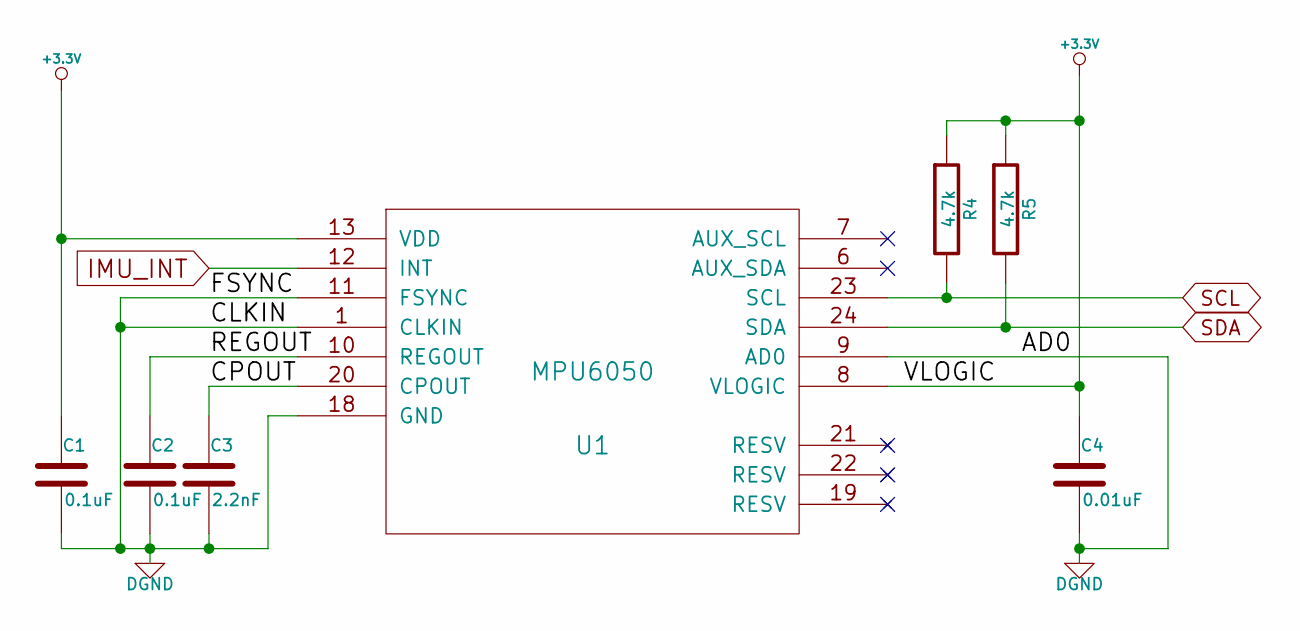
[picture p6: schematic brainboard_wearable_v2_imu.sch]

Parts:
C1, C2: 0.1uF
C3: 2.2nF
C4: 0.01uF
R4, R5: 4.7k
U1: MPU6050

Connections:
+3.3V: C1.1, C4.1, R4.1, R5.1, U1.8 (VLOGIC), U1.13 (VDD); also elsewhere on the board
/Brainboard IMU/CPOUT: C3.1, U1.20 (CPOUT)
/Brainboard IMU/REGOUT: C2.1, U1.10 (REGOUT)
AGND: C1.2, C2.2, C3.2, C4.2, U1.1 (CLKIN), U1.9 (AD0), U1.11 (FSYNC), U1.18 (GND); also elsewhere on the board
IMU_INT: U1.12 (INT); also elsewhere on the board
SCL: R4.2, U1.23 (SCL); also elsewhere on the board
SDA: R5.2, U1.24 (SDA); also elsewhere on the board

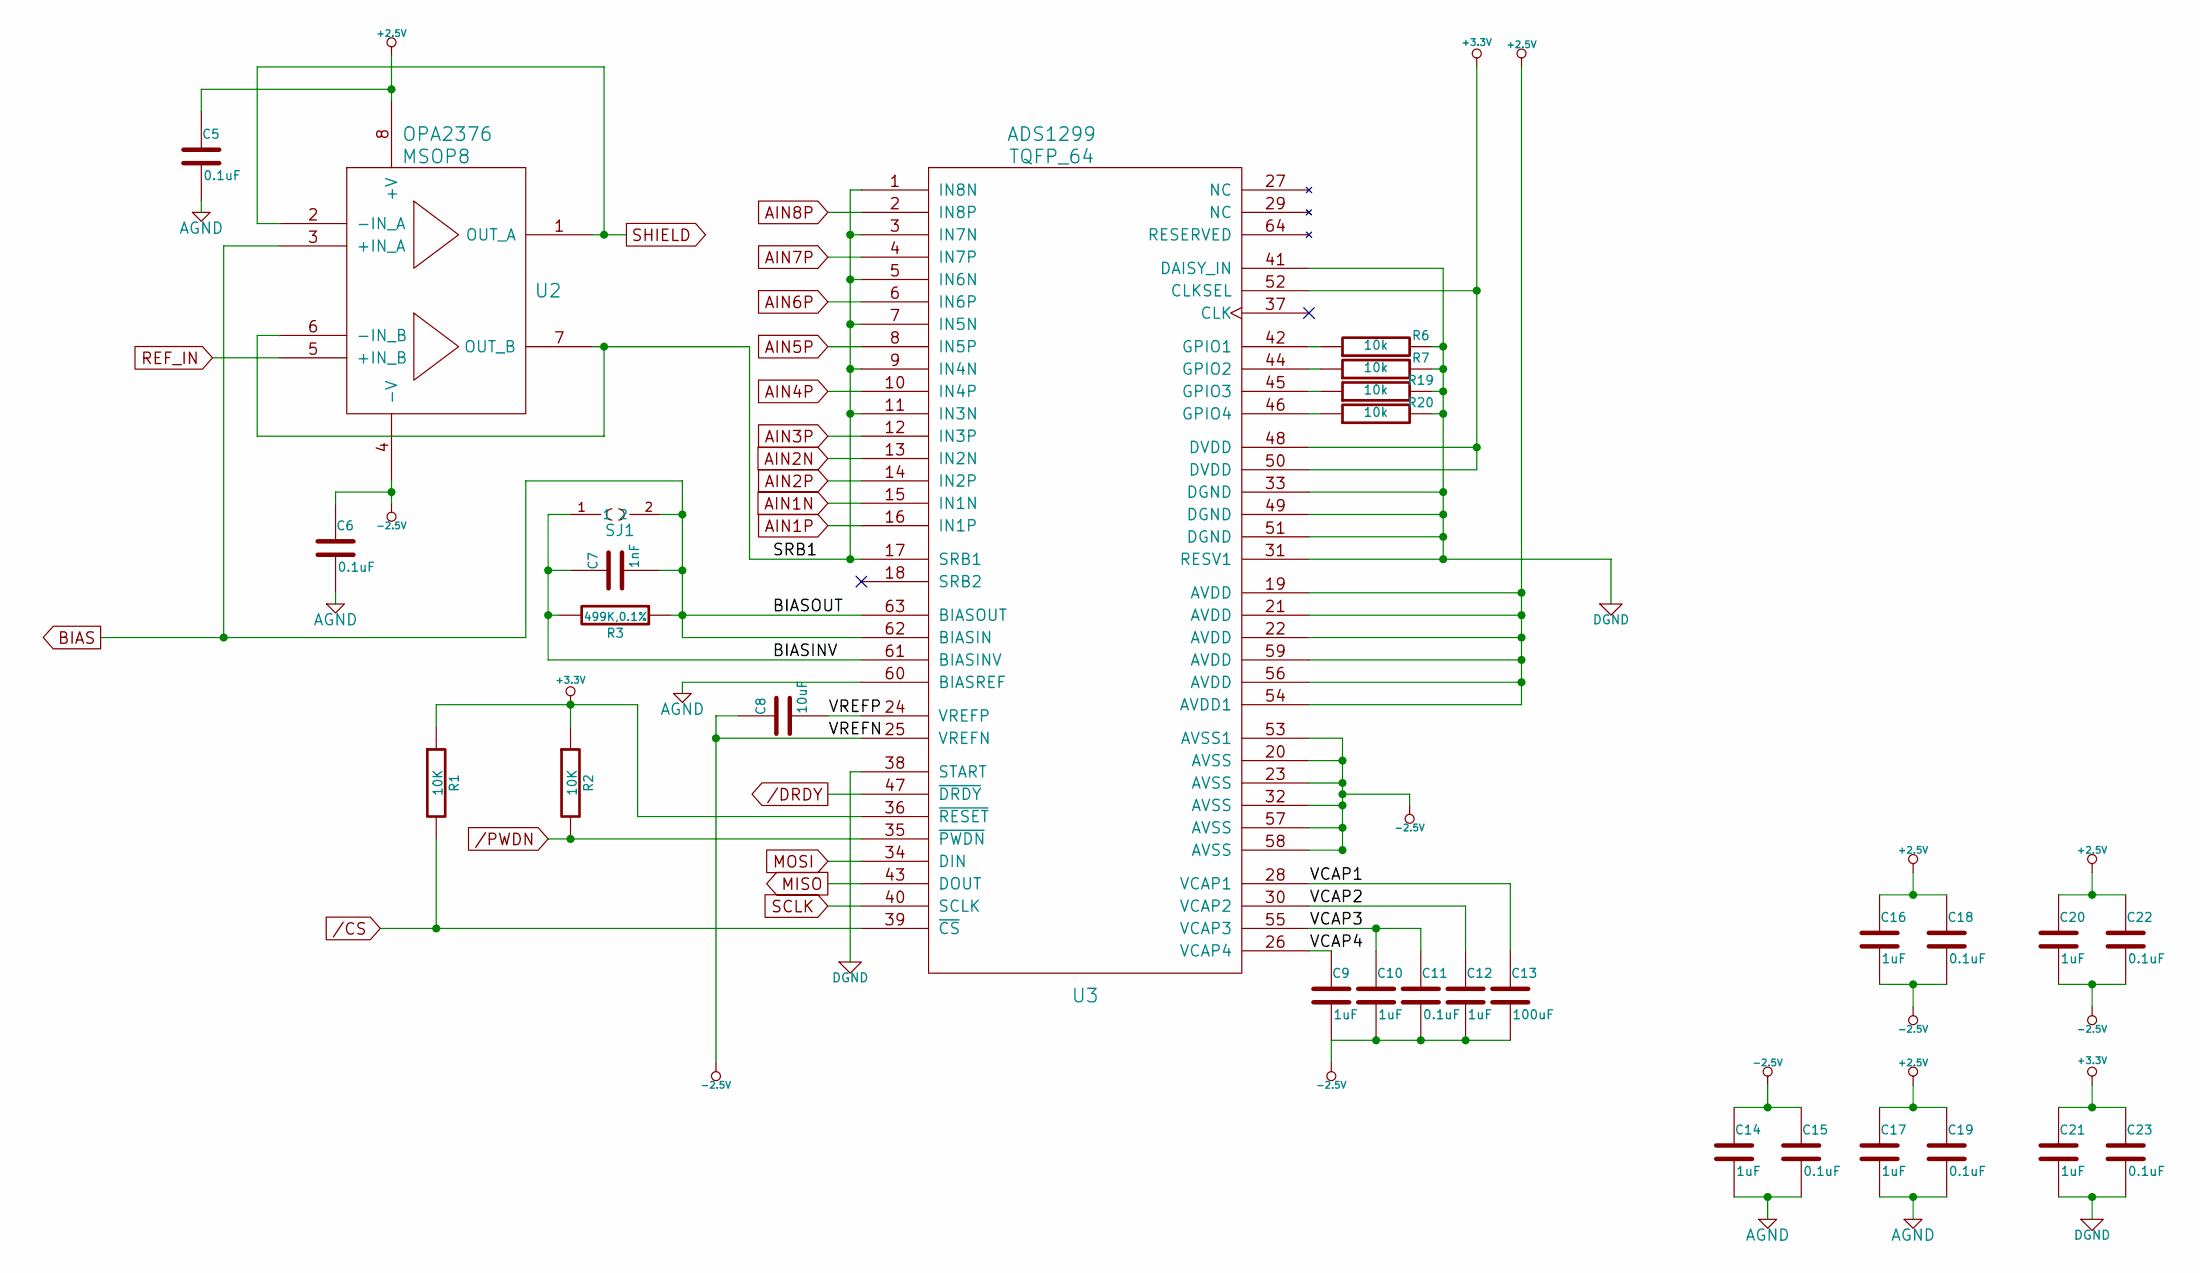
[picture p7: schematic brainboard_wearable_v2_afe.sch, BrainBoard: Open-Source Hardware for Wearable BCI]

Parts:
C5, C6, C11, C15, C18, C19, C22, C23: 0.1uF
C7: 1nF
C8: 10uF
C9, C10, C12, C14, C16, C17, C20, C21: 1uF
C13: 100uF
R1, R2: 10K
R3: 499K,0.1%
R6, R7, R19, R20: 10k
SJ1: NO BIAS FILT; SparkFun-Passives-SJ_2S-NO
U2: OPA2376; MSOP8
U3: ADS1299; TQFP_64

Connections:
+2.5V: C5.1, C16.1, C17.1, C18.1, C19.1, C20.1, C22.1, U2.8 (+V), U3.19 (AVDD), U3.21 (AVDD), U3.22 (AVDD), U3.54 (AVDD1), U3.56 (AVDD), U3.59 (AVDD); also elsewhere on the board
+3.3V: C21.1, C23.1, R1.1, R2.1, U3.36 (~RESET), U3.48 (DVDD), U3.50 (DVDD), U3.52 (CLKSEL); also elsewhere on the board
-2.5V: C6.1, C8.1, C9.2, C10.2, C11.2, C12.2, C13.2, C14.1, C15.1, C16.2, C18.2, C20.2, C22.2, U2.4 (-V), U3.20 (AVSS), U3.23 (AVSS), U3.25 (VREFN), U3.32 (AVSS), U3.53 (AVSS1), U3.57 (AVSS), U3.58 (AVSS); also elsewhere on the board
/Brainboard AFE/BIASINV: C7.1, R3.2, SJ1.1, U3.61 (BIASINV)
/Brainboard AFE/SRB1: U2.6 (-IN_B), U2.7 (OUT_B), U3.1 (IN8N), U3.3 (IN7N), U3.5 (IN6N), U3.7 (IN5N), U3.9 (IN4N), U3.11 (IN3N), U3.17 (SRB1)
/Brainboard AFE/VCAP1: C13.1, U3.28 (VCAP1)
/Brainboard AFE/VCAP2: C12.1, U3.30 (VCAP2)
/Brainboard AFE/VCAP3: C10.1, C11.1, U3.55 (VCAP3)
/Brainboard AFE/VCAP4: C9.1, U3.26 (VCAP4)
/Brainboard AFE/VREFP: C8.2, U3.24 (VREFP)
/CS: R1.2, U3.39 (~CS); also elsewhere on the board
/DRDY: U3.47 (~DRDY); also elsewhere on the board
/PWDN: R2.2, U3.35 (~PWDN); also elsewhere on the board
AGND: C5.2, C6.2, C14.2, C15.2, C17.2, C19.2, C21.2, C23.2, R6.2, R7.2, R19.2, R20.2, U3.31 (RESV1), U3.33 (DGND), U3.38 (START), U3.41 (DAISY_IN), U3.49 (DGND), U3.51 (DGND), U3.60 (BIASREF); also elsewhere on the board
AIN1N: U3.15 (IN1N); also elsewhere on the board
AIN1P: U3.16 (IN1P); also elsewhere on the board
AIN2N: U3.13 (IN2N); also elsewhere on the board
AIN2P: U3.14 (IN2P); also elsewhere on the board
AIN3P: U3.12 (IN3P); also elsewhere on the board
AIN4P: U3.10 (IN4P); also elsewhere on the board
AIN5P: U3.8 (IN5P); also elsewhere on the board
AIN6P: U3.6 (IN6P); also elsewhere on the board
AIN7P: U3.4 (IN7P); also elsewhere on the board
AIN8P: U3.2 (IN8P); also elsewhere on the board
BIAS: C7.2, R3.1, SJ1.2, U2.3 (+IN_A), U3.62 (BIASIN), U3.63 (BIASOUT); also elsewhere on the board
MISO: U3.43 (DOUT); also elsewhere on the board
MOSI: U3.34 (DIN); also elsewhere on the board
unnamed: R20.1, U3.46 (GPIO4)
unnamed: R19.1, U3.45 (GPIO3)
unnamed: R7.1, U3.44 (GPIO2)
unnamed: R6.1, U3.42 (GPIO1)
REF_IN: U2.5 (+IN_B); also elsewhere on the board
SCLK: U3.40 (SCLK); also elsewhere on the board
SHIELD: U2.1 (OUT_A), U2.2 (-IN_A); also elsewhere on the board

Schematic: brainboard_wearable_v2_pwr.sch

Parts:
C24, C31, C42: 0.1uF
C25, C39, C40, C41: 2.2uF
C26, C29, C36, C37, C38: 10uF
C27, C28, C30, C32: 1uF
C33, C34, C35: 0.01uF
CON1: USB
D1: SMAJ7.0A
D2: BATTLO
D3: PGOOD
D4: CHARGE
F1: PTC 500mA
P1: JST
R8: 562k
R9: 51.1k
R10: 383k
R11, R14, R15, R16: 2.2k
R12: 52.3k
R13: 1.18k
S1: DPDT
TH1: NTC 10K
TP1, TP2: GND
TP3: PREREG
TP4: -3V3
TP5: +2V5
TP6: -2V5
TP8: 3V3
U4: LTC1998
U5: BQ24074(T)
U6: TPS60403
U7: TPS73233
U8: TPS73225
U9: TPS72325

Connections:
+2.5V: C36.1, C39.1, C42.1, TP5.1, U8.5; also elsewhere on the board
+3.3V: C27.1, C32.1, C38.1, C41.1, D2.1 (A), TP8.1, U4.5 (VLOGIC), U6.2 (IN), U7.5, U8.1, U8.3; also elsewhere on the board
+BATT: C24.1, C26.1, R8.1, S1.2, S1.5, U4.1 (BATT), U5.2 (BAT), U5.3 (BAT)
-2.5V: C37.1, C40.1, C42.2, TP6.1, U9.5 (OUT); also elsewhere on the board
-3.3V: C30.1, TP4.1, U6.1 (OUT), U9.2 (IN), U9.3 (EN)
/BATTLO: R11.1, U4.6 (~BATTLO); also elsewhere on the board
/Brainboard Power/B+: F1.2, P1.1
/Brainboard Power/ILIM: R13.1, U5.12 (ILIM)
/Brainboard Power/ISET: R14.1, U5.16 (ISET)
/Brainboard Power/OUT: C29.1, C31.1, R15.1, R16.1, TP3.1, U5.6 (EN1), U5.10 (OUT), U5.11 (OUT), U7.1, U7.3
/Brainboard Power/TMR: R12.1, U5.14 (TMR)
/Brainboard Power/TS: TH1.1, U5.1 (TS)
/Brainboard Power/VBUS: C25.1, CON1.1 (VBUS), D1.2 (K), U5.13 (IN)
/Brainboard Power/_B+: F1.1, S1.1, S1.4
/Brainboard Power/~CHG: D4.2 (K), U5.9 (~CHG)
/Brainboard Power/~PGOOD: D3.2 (K), U5.7 (~PGOOD)
AGND: C24.2, C25.2, C26.2, C27.2, C29.2, C30.2, C31.2, C32.2, C33.2, C34.2, C35.2, C36.2, C37.2, C38.2, C39.2, C40.2, C41.2, CON1.5 (GND), CON1.6 (SHELL1), CON1.7 (SHELL2), CON1.8 (SHELL3), CON1.9 (SHELL4), D1.1 (A), P1.2 (PM), R10.2, R12.2, R13.2, R14.2, TH1.2, TP1.1, TP2.1, U4.2 (GND), U5.4 (~CE), U5.5 (EN2), U5.8 (VSS), U5.15 (TD/ITERM/SYSOFF), U5.17 (PWPD), U6.4 (GND), U7.2, U8.2, U9.1 (GND); also elsewhere on the board
unnamed: C33.1, U7.4
unnamed: D3.1 (A), R16.2
unnamed: D4.1 (A), R15.2
unnamed: R9.2, R10.1, U4.4 (VHA)
unnamed: R8.2, R9.1, U4.3 (VTHA)
unnamed: D2.2 (K), R11.2
unnamed: C28.2, U6.3 (CFLY-)
unnamed: C28.1, U6.5 (CFLY+)
unnamed: C34.1, U8.4
unnamed: C35.1, U9.4 (NR)

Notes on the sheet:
Battery charger
3.3V regulation
Fast charging current = K_ISET/R_ISET K_ISET = [797..975], 890 typical R_ISET = 2.2k yields 404mA, or 0.4C for 1000mAh cell Input current limit = 500 mA (EN1 = H, EN2 = L)
T_MAXCHG = 10*K_TMR*R_TMR K_TMR = 48s/kOhm R_TMR = 52.3k gives about 7 hr safety cutoff
BATTLO threshold at 3.1V w/ 100mV hysteresis
Low battery detection
Bipolar analog supply generation

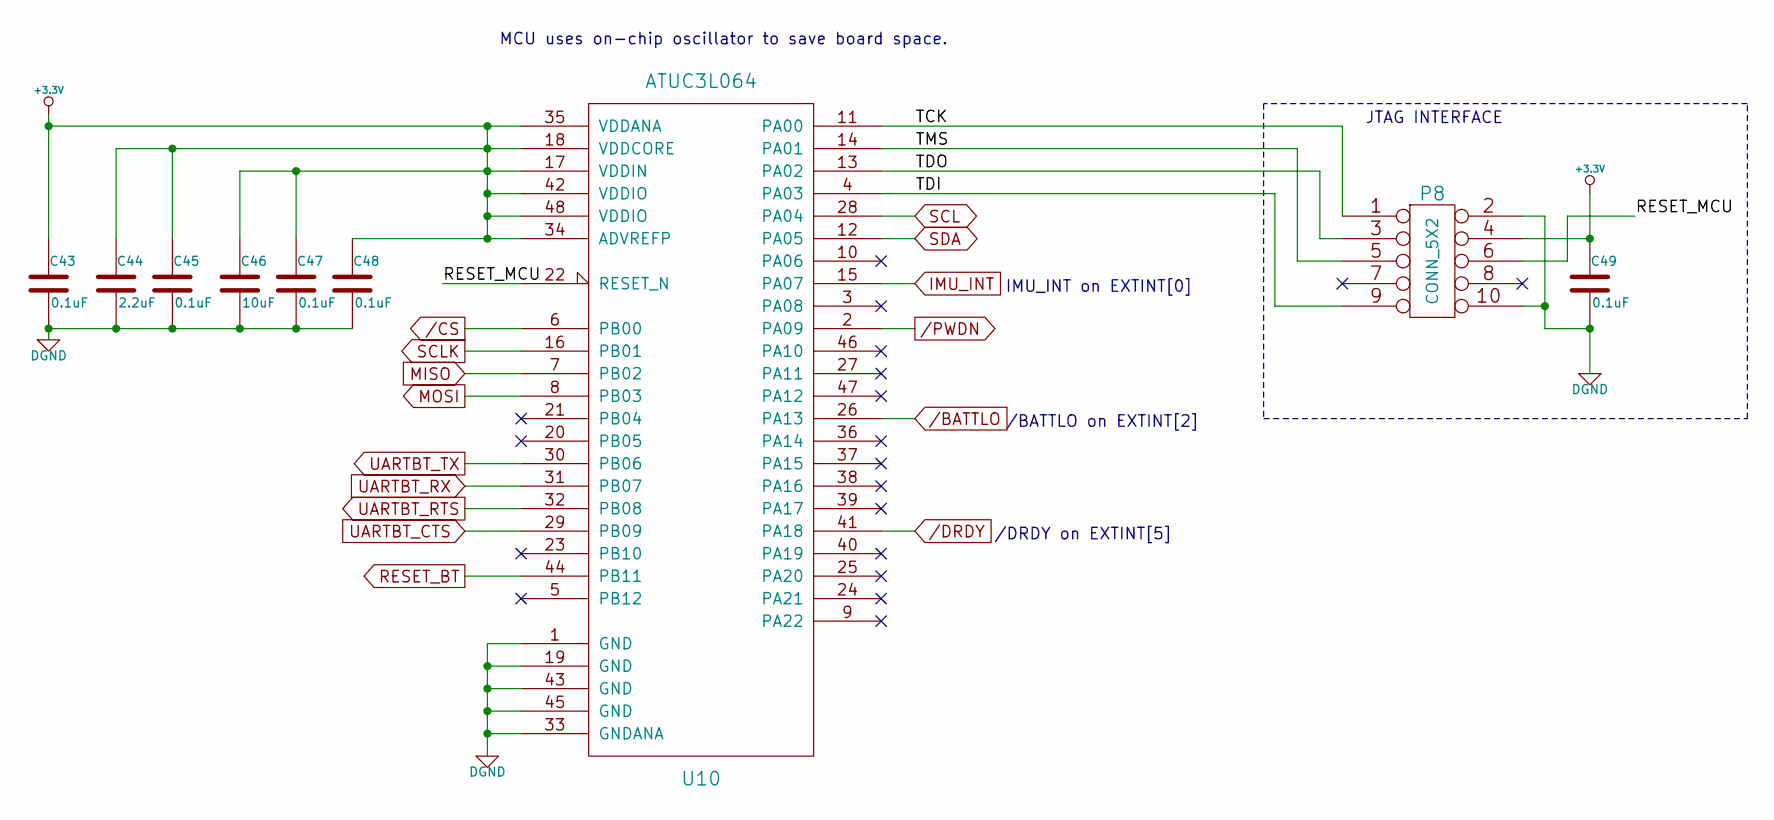
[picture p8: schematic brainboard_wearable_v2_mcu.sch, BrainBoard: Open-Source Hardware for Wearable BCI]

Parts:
C43, C45, C47, C48, C49: 0.1uF
C44: 2.2uF
C46: 10uF
P8: CONN_5X2
U10: ATUC3L064

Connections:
+3.3V: C43.1, C44.1, C45.1, C46.1, C47.1, C48.1, C49.1, P8.4, U10.17 (VDDIN), U10.18 (VDDCORE), U10.34 (ADVREFP), U10.35 (VDDANA), U10.42 (VDDIO), U10.48 (VDDIO); also elsewhere on the board
/BATTLO: U10.26 (PA13); also elsewhere on the board
/Brainboard MCU/RESET_MCU: P8.6, U10.22 (RESET_N)
/Brainboard MCU/TCK: P8.1, U10.11 (PA00)
/Brainboard MCU/TDI: P8.9, U10.4 (PA03)
/Brainboard MCU/TDO: P8.3, U10.13 (PA02)
/Brainboard MCU/TMS: P8.5, U10.14 (PA01)
/CS: U10.6 (PB00); also elsewhere on the board
/DRDY: U10.41 (PA18); also elsewhere on the board
/PWDN: U10.2 (PA09); also elsewhere on the board
AGND: C43.2, C44.2, C45.2, C46.2, C47.2, C48.2, C49.2, P8.2, P8.10, U10.1 (GND), U10.19 (GND), U10.33 (GNDANA), U10.43 (GND), U10.45 (GND); also elsewhere on the board
IMU_INT: U10.15 (PA07); also elsewhere on the board
MISO: U10.7 (PB02); also elsewhere on the board
MOSI: U10.8 (PB03); also elsewhere on the board
RESET_BT: U10.44 (PB11); also elsewhere on the board
SCL: U10.28 (PA04); also elsewhere on the board
SCLK: U10.16 (PB01); also elsewhere on the board
SDA: U10.12 (PA05); also elsewhere on the board
UARTBT_CTS: U10.29 (PB09); also elsewhere on the board
UARTBT_RTS: U10.32 (PB08); also elsewhere on the board
UARTBT_RX: U10.31 (PB07); also elsewhere on the board
UARTBT_TX: U10.30 (PB06); also elsewhere on the board

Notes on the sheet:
JTAG INTERFACE
MCU uses on-chip oscillator to save board space.
/DRDY on EXTINT[5]
IMU_INT on EXTINT[0]
/BATTLO on EXTINT[2]

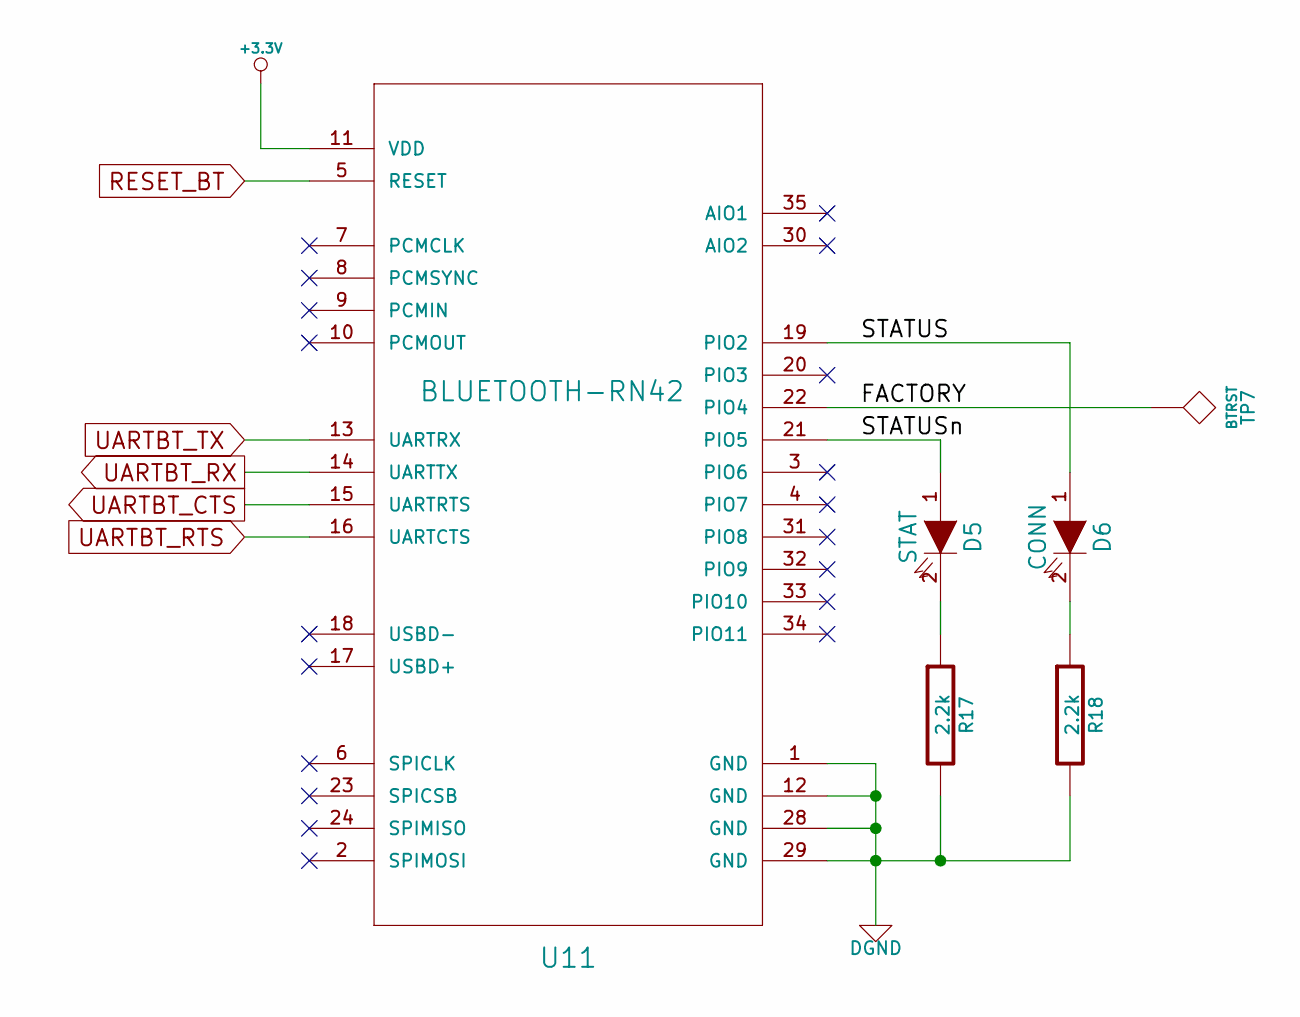
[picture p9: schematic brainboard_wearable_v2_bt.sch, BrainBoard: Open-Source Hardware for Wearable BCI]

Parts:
D5: STAT
D6: CONN
R17, R18: 2.2k
TP7: BTRST
U11: BLUETOOTH-RN42

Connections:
+3.3V: U11.11 (VDD); also elsewhere on the board
/Brainboard Bluetooth/FACTORY: TP7.1, U11.22 (PIO4)
/Brainboard Bluetooth/STATUS: D6.1 (A), U11.19 (PIO2)
/Brainboard Bluetooth/STATUSn: D5.1 (A), U11.21 (PIO5)
AGND: R17.2, R18.2, U11.1 (GND), U11.12 (GND), U11.28 (GND), U11.29 (GND); also elsewhere on the board
unnamed: D6.2 (K), R18.1
unnamed: D5.2 (K), R17.1
RESET_BT: U11.5 (RESET); also elsewhere on the board
UARTBT_CTS: U11.15 (UARTRTS); also elsewhere on the board
UARTBT_RTS: U11.16 (UARTCTS); also elsewhere on the board
UARTBT_RX: U11.14 (UARTTX); also elsewhere on the board
UARTBT_TX: U11.13 (UARTRX); also elsewhere on the board

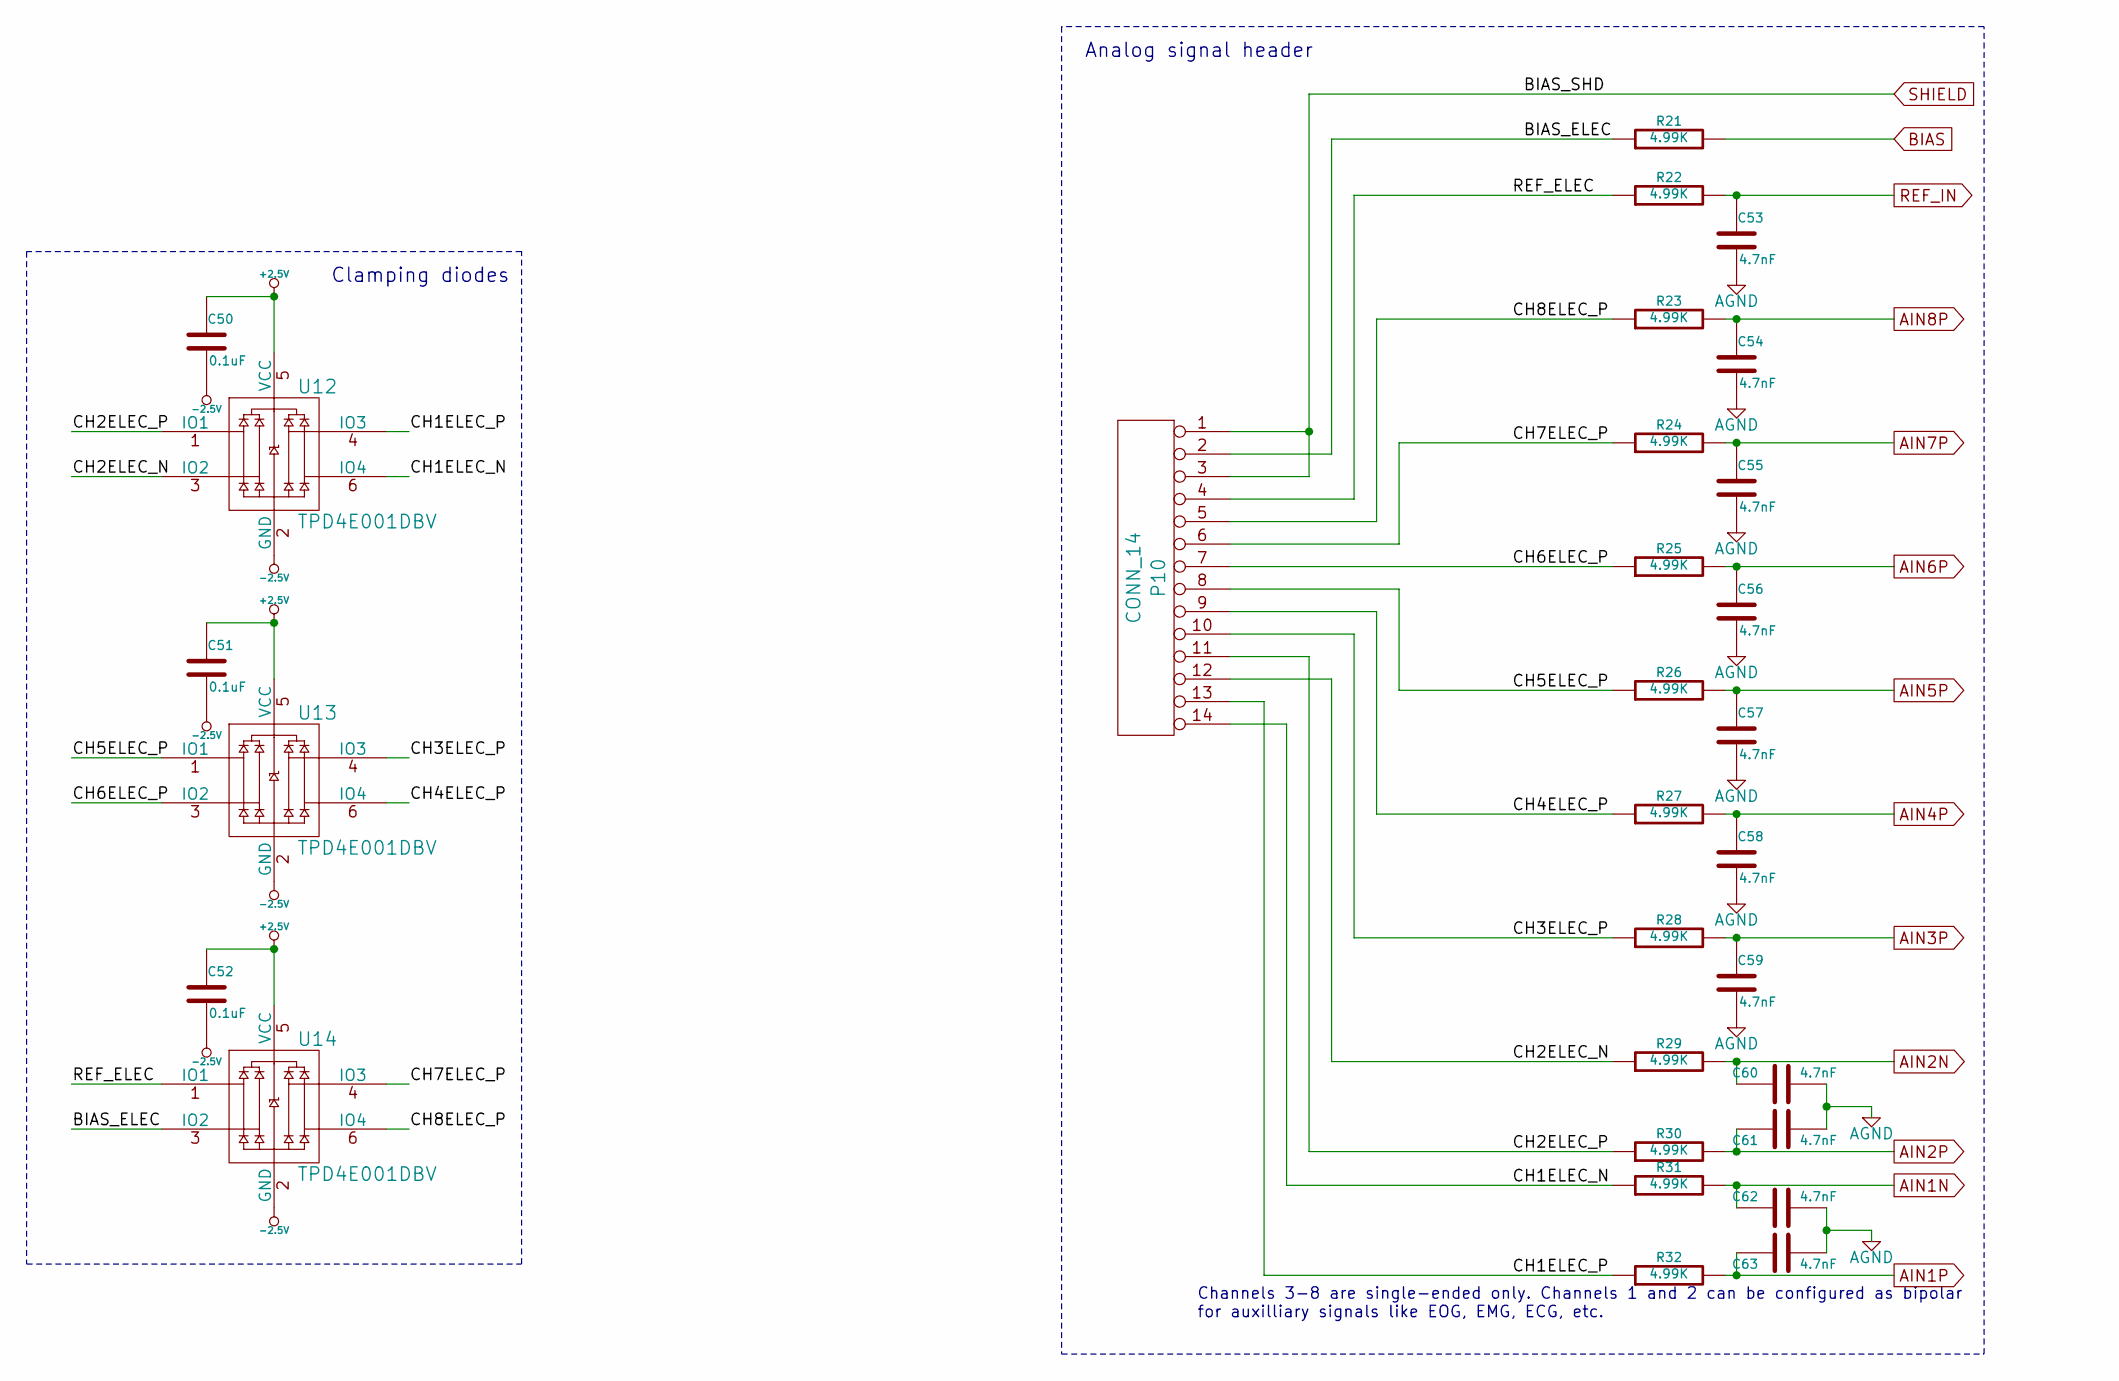
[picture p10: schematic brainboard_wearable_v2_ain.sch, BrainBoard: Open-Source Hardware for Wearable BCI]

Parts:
C50, C51, C52: 0.1uF
C53, C54, C55, C56, C57, C58, C59, C60, C61, C62, C63: 4.7nF
P10: CONN_14
R21, R22, R23, R24, R25, R26, R27, R28, R29, R30, R31, R32: 4.99K
U12, U13, U14: TPD4E001DBV

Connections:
+2.5V: C50.1, C51.1, C52.1, U12.5 (VCC), U13.5 (VCC), U14.5 (VCC); also elsewhere on the board
-2.5V: C50.2, C51.2, C52.2, U12.2 (GND), U13.2 (GND), U14.2 (GND); also elsewhere on the board
/Brainboard Analog In/BIAS_ELEC: P10.2, R21.1, U14.3 (IO2)
/Brainboard Analog In/CH1ELEC_N: P10.14, R31.1, U12.6 (IO4)
/Brainboard Analog In/CH1ELEC_P: P10.13, R32.1, U12.4 (IO3)
/Brainboard Analog In/CH2ELEC_N: P10.12, R29.1, U12.3 (IO2)
/Brainboard Analog In/CH2ELEC_P: P10.11, R30.1, U12.1 (IO1)
/Brainboard Analog In/CH3ELEC_P: P10.10, R28.1, U13.4 (IO3)
/Brainboard Analog In/CH4ELEC_P: P10.9, R27.1, U13.6 (IO4)
/Brainboard Analog In/CH5ELEC_P: P10.8, R26.1, U13.1 (IO1)
/Brainboard Analog In/CH6ELEC_P: P10.7, R25.1, U13.3 (IO2)
/Brainboard Analog In/CH7ELEC_P: P10.6, R24.1, U14.4 (IO3)
/Brainboard Analog In/CH8ELEC_P: P10.5, R23.1, U14.6 (IO4)
/Brainboard Analog In/REF_ELEC: P10.4, R22.1, U14.1 (IO1)
AGND: C53.2, C54.2, C55.2, C56.2, C57.2, C58.2, C59.2, C60.2, C61.2, C62.2, C63.2; also elsewhere on the board
AIN1N: C62.1, R31.2; also elsewhere on the board
AIN1P: C63.1, R32.2; also elsewhere on the board
AIN2N: C60.1, R29.2; also elsewhere on the board
AIN2P: C61.1, R30.2; also elsewhere on the board
AIN3P: C59.1, R28.2; also elsewhere on the board
AIN4P: C58.1, R27.2; also elsewhere on the board
AIN5P: C57.1, R26.2; also elsewhere on the board
AIN6P: C56.1, R25.2; also elsewhere on the board
AIN7P: C55.1, R24.2; also elsewhere on the board
AIN8P: C54.1, R23.2; also elsewhere on the board
BIAS: R21.2; also elsewhere on the board
REF_IN: C53.1, R22.2; also elsewhere on the board
SHIELD: P10.1, P10.3; also elsewhere on the board

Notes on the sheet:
Clamping diodes
Analog signal header
Channels 3-8 are single-ended only. Channels 1 and 2 can be configured as bipolar for auxilliary signals like EOG, EMG, ECG, etc.

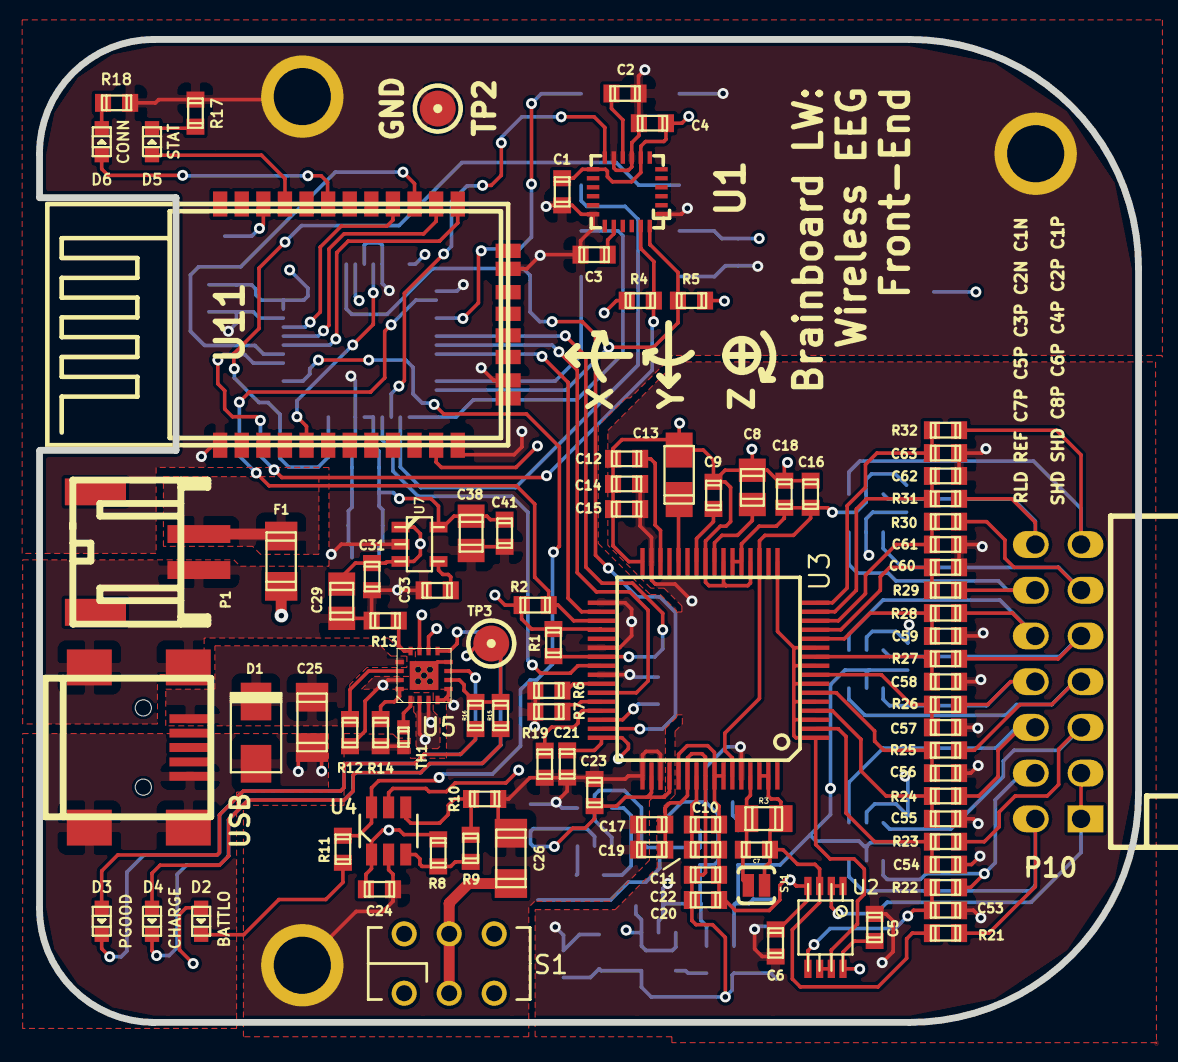
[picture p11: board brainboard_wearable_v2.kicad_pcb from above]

Board: 4 copper layers, 61.1 x 54.6 mm, 134 parts (0 on the bottom side), 89 nets.

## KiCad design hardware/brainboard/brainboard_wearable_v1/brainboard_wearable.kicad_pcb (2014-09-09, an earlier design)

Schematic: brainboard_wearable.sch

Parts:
BT1: LIR2450
C1, C2, C9, C11, C14: 0.1uF
C3, C6, C15: 10uF
C4, C5: 30pF
C8, C10, C16, C17: 1uF
C12, C13: 4.7nF
C18: 1.5nF
FB1: BLM18PG121SN1
P1: CONN_3X2
P2: ICSP
R1: 10k
R2: 51k
R3: 1M
S1: DPDT
TP1: FACT
TP2: STATUS
U1: ATMEGA328P-28PIN
U2: ADS1291/2
U3: BLUETOOTH-RN42
Y1: ABM3B-8.000MHZ

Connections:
+BATT: BT1.1 (+), C3.1, C6.1, S1.1, S1.4
/AREF: C1.1, U1.17
/BT_CONN: U1.21, U3.19 (PIO2)
/BT_RESET: U1.20, U3.5 (RESET)
/FACTORY_RESET: TP1.1, U1.19, U3.22 (PIO4)
/MCU_RX: U1.26, U3.14 (UARTTX)
/MCU_TX: U1.27, U3.13 (UARTRX)
/PGA1N: C12.2, U2.1 (PGA1N)
/PGA1P: C12.1, U2.2 (PGA1P)
/PGA2N: C13.2, U2.7 (PGA2N)
/PGA2P: C13.1, U2.8 (PGA2P)
/RLDIN: C18.1, R2.1, R3.1, U2.29 (RLDIN/RLDREF), U2.30 (RLDOUT)
/RLDINV: C18.2, R3.2, U2.28 (RLDINV)
/STATUS: TP2.1, U3.21 (PIO5)
/VCAP1: C17.1, U2.11 (VCAP1)
/VCAP2: C16.1, U2.27 (VCAP2)
/VREFP: C14.1, C15.1, U2.9 (VREFP)
/~MCU_CTS: U1.1, U3.15 (UARTRTS)
/~MCU_RTS: U1.2, U3.16 (UARTCTS)
AVDD: C8.1, C9.1, FB1.2, U2.12 (AVDD), U2.31 (RESP_MODP), U2.32 (RESP_MODN)
CH1N: P1.3, U2.3 (IN1N)
CH1P: P1.4, U2.4 (IN1P)
CH2N: P1.5, U2.5 (IN2N)
CH2P: P1.6, U2.6 (IN2P)
DVDD: C2.1, C10.1, C11.1, FB1.1, R1.1, U1.3, U1.16, U2.23 (DVDD), U3.11 (VDD); also elsewhere on the board
GND: BT1.2 (-), C1.2, C2.2, C3.2, C4.1, C5.1, C6.2, C8.2, C9.2, C10.2, C11.2, C14.2, C15.2, C16.2, C17.2, P2.6, U1.4, U1.18, U1.29, U2.10 (VREFN), U2.13 (AVSS), U2.24 (DGND), U2.33 (PAD), U3.1 (GND), U3.12 (GND), U3.28 (GND), U3.29 (GND); also elsewhere on the board
MISO: P2.1, U1.14, U2.21 (DOUT)
MOSI: P2.4, U1.13, U2.19 (DIN)
unnamed: C5.2, U1.6, Y1.2
unnamed: C4.2, U1.5, Y1.1
RLD: P1.2, R2.2
SCLK: P2.3, U1.15, U2.20 (SCLK)
VCC: S1.2, S1.5; also elsewhere on the board
VEXT: P2.2, S1.3, S1.6
~AFE_CS: U1.11, U2.18 (~CS)
~AFE_DRDY: U1.28, U2.22 (~DRDY)
~AFE_PWDN: U1.7, U2.15 (~PWDN~/~RESET)
~MCU_RESET: P2.5, R1.2, U1.25

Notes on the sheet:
ISP Programming - NI
Power
VCAP1 should connect to Class 1 ceramic or tantalum capacitor to avoid ferroelectric noise.
Electrode connector
Front-end
Supply filtering
Microcontroller
Bluetooth

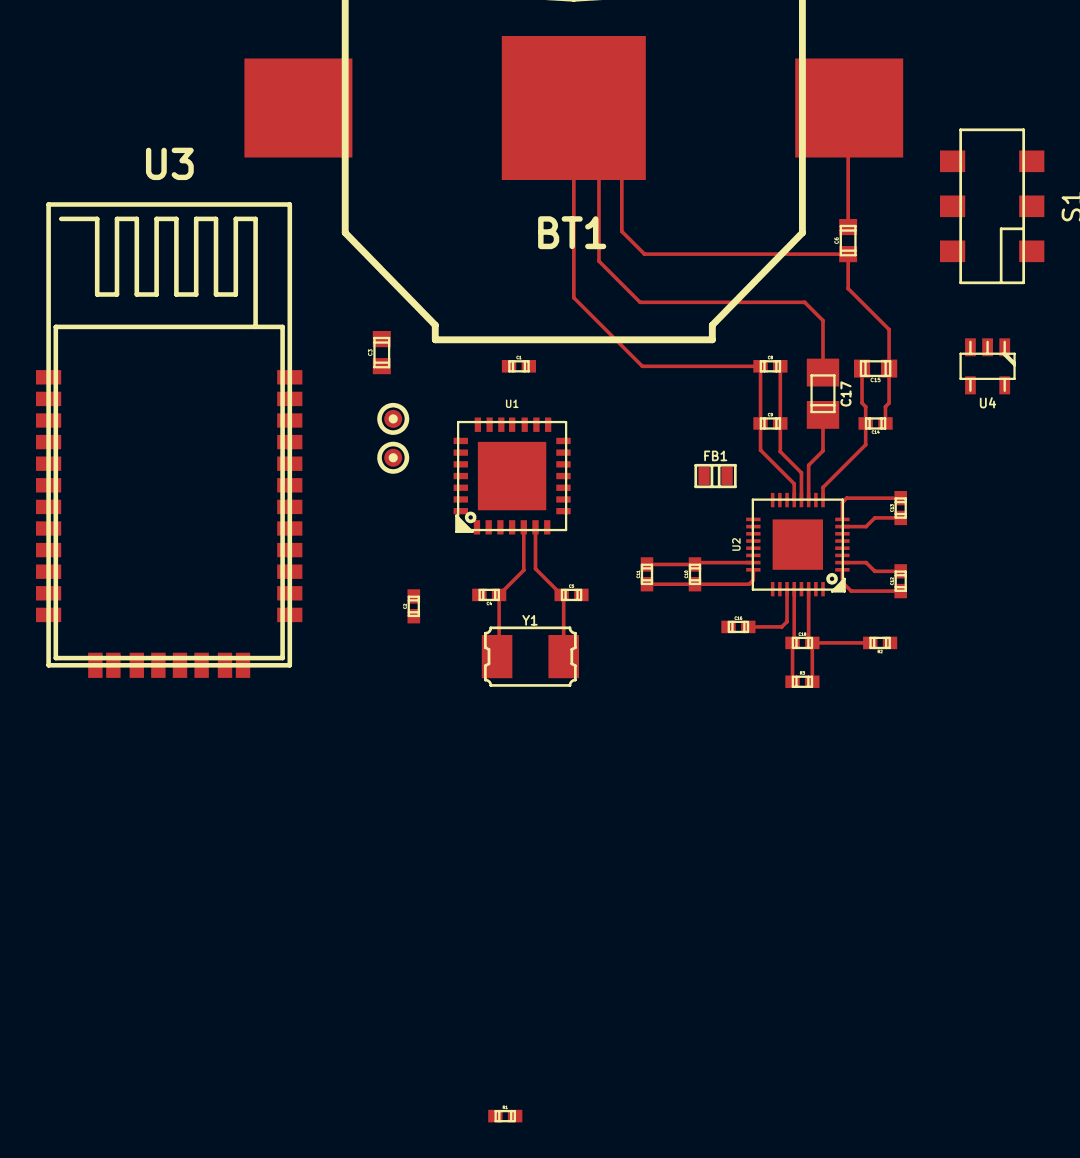
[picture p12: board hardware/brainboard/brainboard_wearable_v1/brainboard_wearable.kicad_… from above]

Board: 2 copper layers, 30 parts (0 on the bottom side), 33 nets.

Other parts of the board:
U4: TPS73233; sot23-5

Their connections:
DVDD: U4.5; also elsewhere on the board
GND: U4.2; also elsewhere on the board
VCC: U4.1, U4.3; also elsewhere on the board

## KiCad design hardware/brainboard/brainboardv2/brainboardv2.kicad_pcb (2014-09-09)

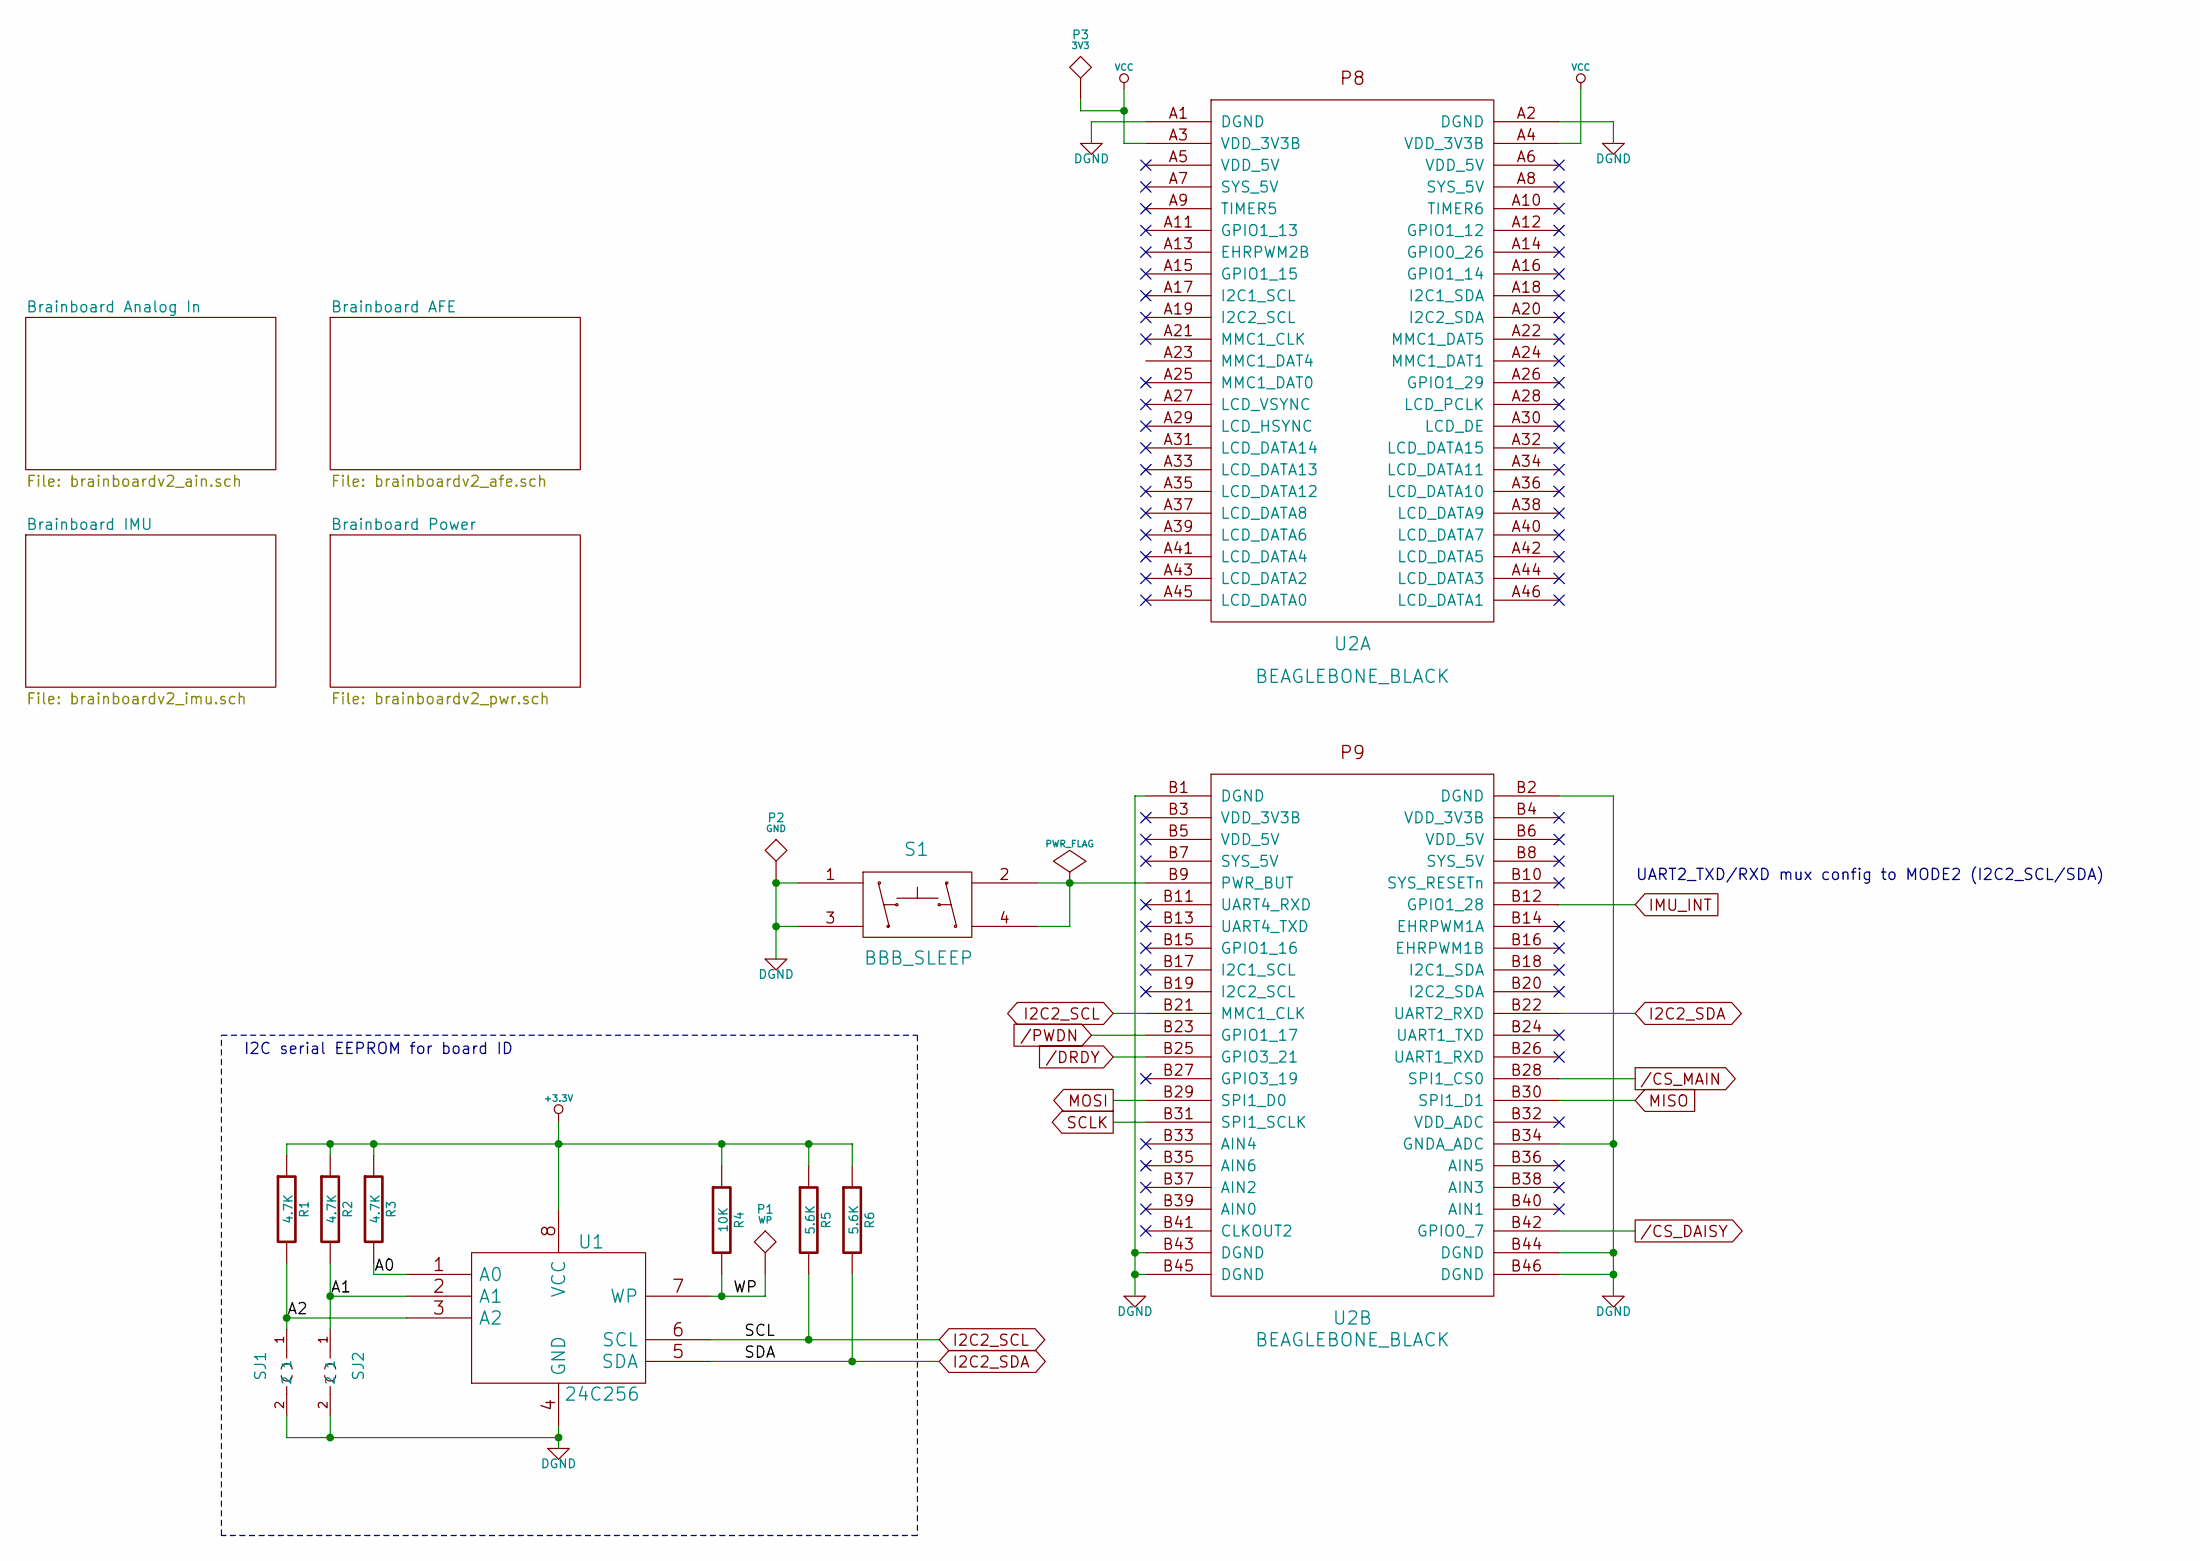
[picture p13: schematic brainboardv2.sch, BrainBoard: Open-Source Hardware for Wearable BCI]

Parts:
P1: WP
P2: GND
P3: 3V3
R1, R2, R3: 4.7K
R4: 10K
R5, R6: 5.6K
S1: BBB_SLEEP
SJ1: A2; SparkFun-Passives-SJ_2S-NOTRACE
SJ2: A1; SparkFun-Passives-SJ_2S-NOTRACE
U1: 24C256
U2: BEAGLEBONE_BLACK

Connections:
+3.3V: R1.1, R2.1, R3.1, R4.1, R5.1, R6.1, U1.8 (VCC); also elsewhere on the board
/A0: R3.2, U1.1 (A0)
/A1: R2.2, SJ2.1, U1.2 (A1)
/A2: R1.2, SJ1.1, U1.3 (A2)
/CS_DAISY: U2.B42 (GPIO0_7); also elsewhere on the board
/CS_MAIN: U2.B28 (SPI1_CS0); also elsewhere on the board
/DRDY: U2.B25 (GPIO3_21); also elsewhere on the board
/PWDN: U2.B23 (GPIO1_17); also elsewhere on the board
/WP: P1.1, R4.2, U1.7 (WP)
AGND: P2.1, S1.1, S1.3, SJ1.2, SJ2.2, U1.4 (GND), U2.A1 (DGND), U2.A2 (DGND), U2.B1 (DGND), U2.B2 (DGND), U2.B34 (GNDA_ADC), U2.B43 (DGND), U2.B44 (DGND), U2.B45 (DGND), U2.B46 (DGND); also elsewhere on the board
I2C2_SCL: R5.2, U1.6 (SCL), U2.B21 (MMC1_CLK); also elsewhere on the board
I2C2_SDA: R6.2, U1.5 (SDA), U2.B22 (UART2_RXD); also elsewhere on the board
IMU_INT: U2.B12 (GPIO1_28); also elsewhere on the board
MISO: U2.B30 (SPI1_D1); also elsewhere on the board
MOSI: U2.B29 (SPI1_D0); also elsewhere on the board
unnamed: S1.2, S1.4, U2.B9 (PWR_BUT)
SCLK: U2.B31 (SPI1_SCLK); also elsewhere on the board
VCC: P3.1, U2.A3 (VDD_3V3B), U2.A4 (VDD_3V3B); also elsewhere on the board

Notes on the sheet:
I2C serial EEPROM for board ID
UART2_TXD/RXD mux config to MODE2 (I2C2_SCL/SDA)

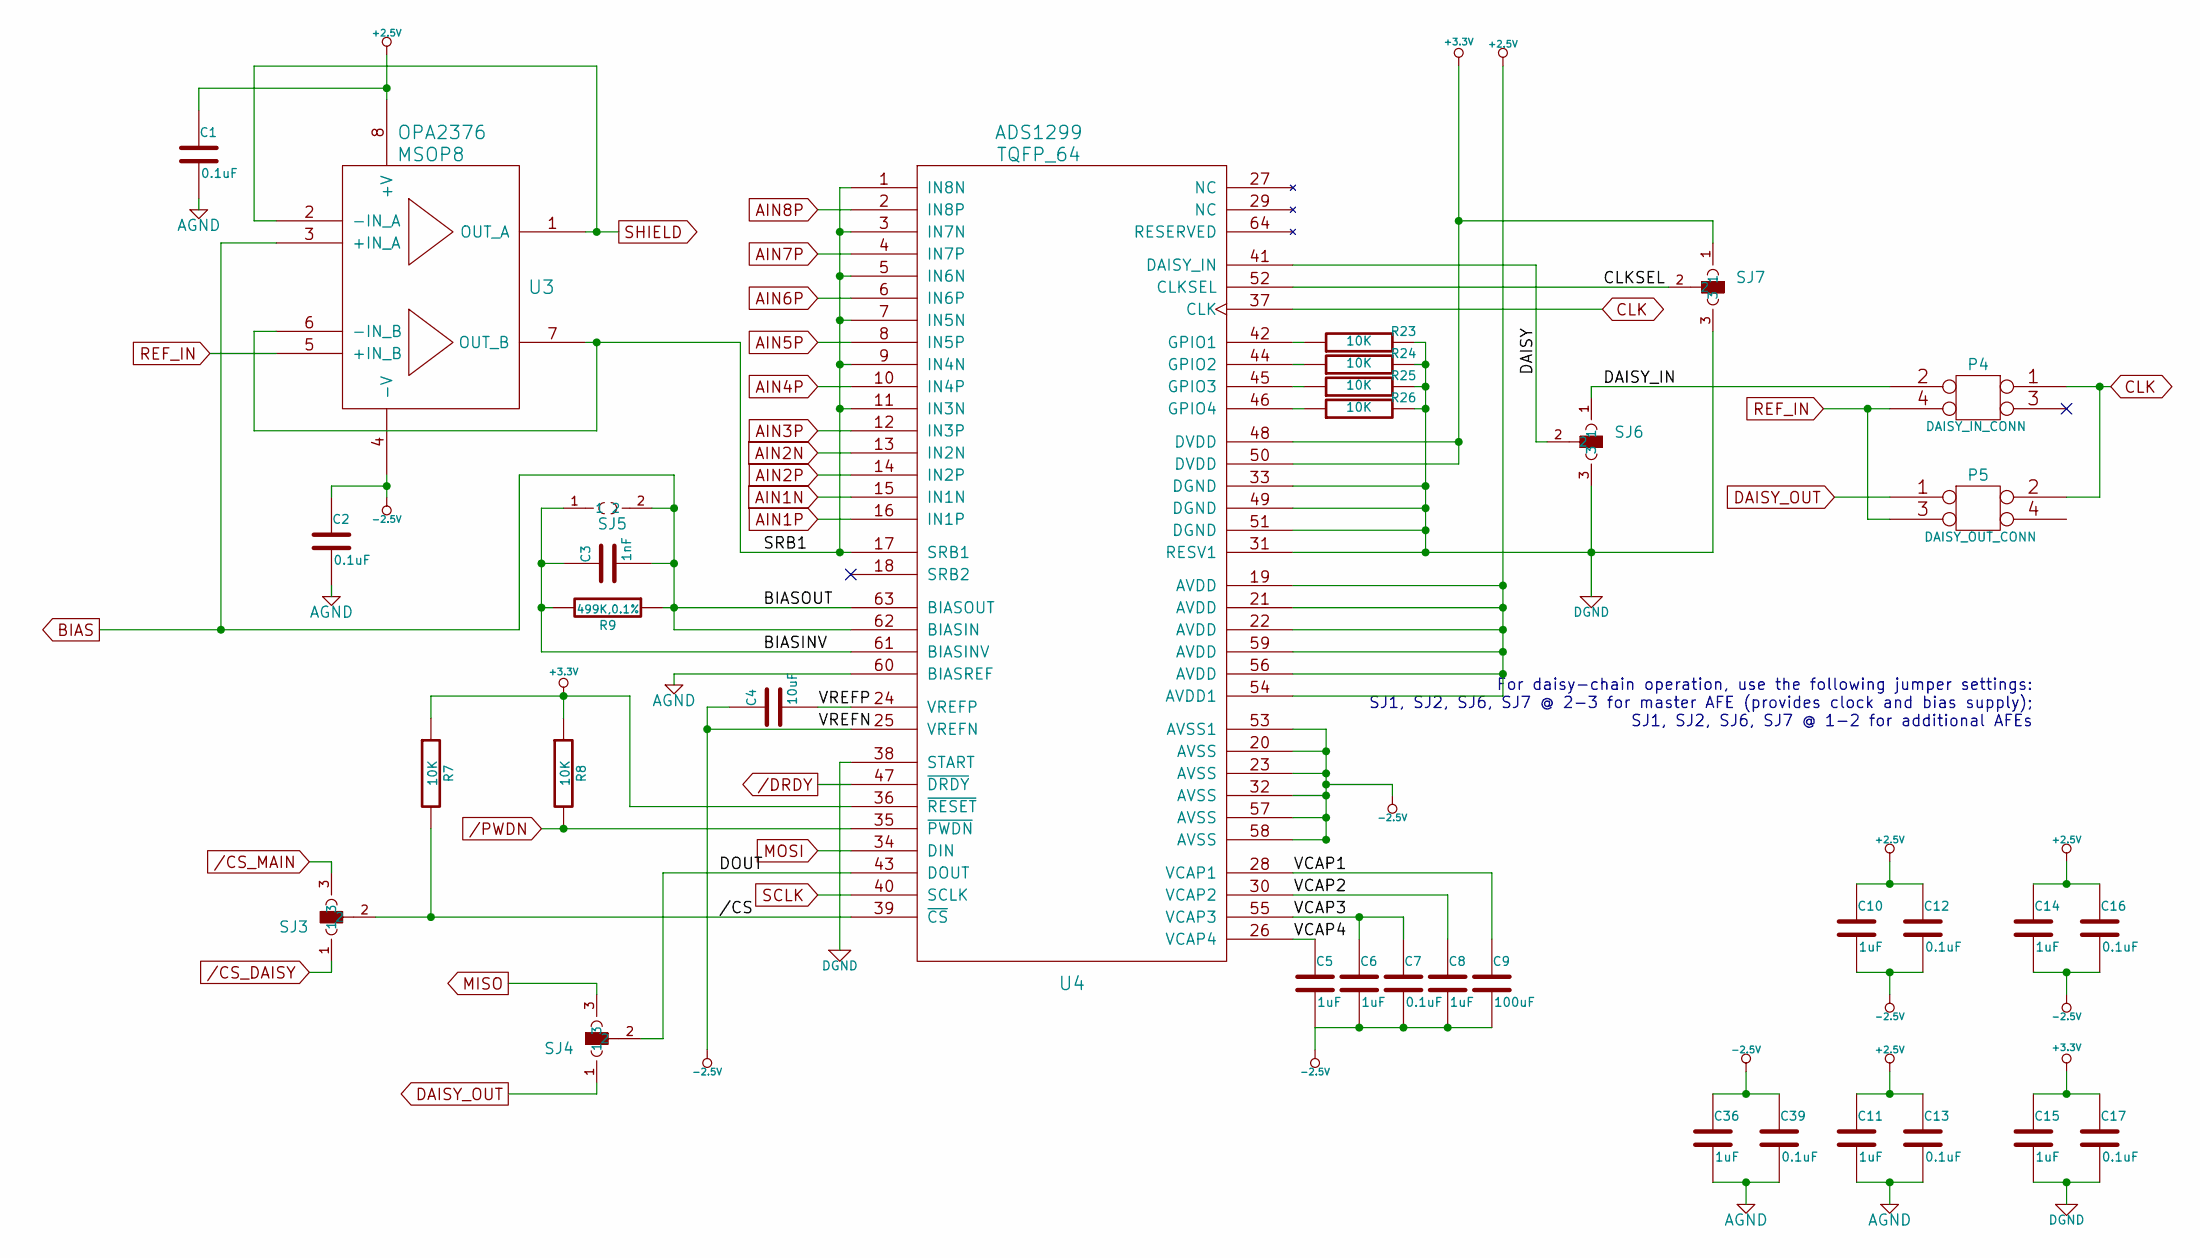
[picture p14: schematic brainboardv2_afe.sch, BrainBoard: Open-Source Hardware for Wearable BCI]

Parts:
C1, C2, C7, C12, C13, C16, C17, C39: 0.1uF
C3: 1nF
C4: 10uF
C5, C6, C8, C10, C11, C14, C15, C36: 1uF
C9: 100uF
P4: DAISY_IN_CONN
P5: DAISY_OUT_CONN
R7, R8, R23, R24, R25, R26: 10K
R9: 499K,0.1%
SJ3, SJ6: DAISY_CS; SparkFun-Passives-SJ_3_PASTE2&3
SJ4: DAISY_OUT; SparkFun-Passives-SJ_3_PASTE2&3
SJ5: NO BIAS FILT; SparkFun-Passives-SJ_2S-NO
SJ7: CLKSEL; SparkFun-Passives-SJ_3_PASTE1&2
U3: OPA2376; MSOP8
U4: ADS1299; TQFP_64

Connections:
+2.5V: C1.1, C10.1, C11.1, C12.1, C13.1, C14.1, C16.1, U3.8 (+V), U4.19 (AVDD), U4.21 (AVDD), U4.22 (AVDD), U4.54 (AVDD1), U4.56 (AVDD), U4.59 (AVDD); also elsewhere on the board
+3.3V: C15.1, C17.1, R7.1, R8.1, SJ7.1, U4.36 (~RESET), U4.48 (DVDD), U4.50 (DVDD); also elsewhere on the board
-2.5V: C2.1, C4.1, C5.2, C6.2, C7.2, C8.2, C9.2, C10.2, C12.2, C14.2, C16.2, C36.1, C39.1, U3.4 (-V), U4.20 (AVSS), U4.23 (AVSS), U4.25 (VREFN), U4.32 (AVSS), U4.53 (AVSS1), U4.57 (AVSS), U4.58 (AVSS); also elsewhere on the board
/Brainboard AFE//CS: R7.2, SJ3.2, U4.39 (~CS)
/Brainboard AFE/BIASINV: C3.1, R9.2, SJ5.1, U4.61 (BIASINV)
/Brainboard AFE/CLKSEL: SJ7.2, U4.52 (CLKSEL)
/Brainboard AFE/DAISY: SJ6.2, U4.41 (DAISY_IN)
/Brainboard AFE/DAISY_IN: P4.2, SJ6.1
/Brainboard AFE/DOUT: SJ4.2, U4.43 (DOUT)
/Brainboard AFE/SRB1: U3.6 (-IN_B), U3.7 (OUT_B), U4.1 (IN8N), U4.3 (IN7N), U4.5 (IN6N), U4.7 (IN5N), U4.9 (IN4N), U4.11 (IN3N), U4.17 (SRB1)
/Brainboard AFE/VCAP1: C9.1, U4.28 (VCAP1)
/Brainboard AFE/VCAP2: C8.1, U4.30 (VCAP2)
/Brainboard AFE/VCAP3: C6.1, C7.1, U4.55 (VCAP3)
/Brainboard AFE/VCAP4: C5.1, U4.26 (VCAP4)
/Brainboard AFE/VREFP: C4.2, U4.24 (VREFP)
/CS_DAISY: SJ3.1; also elsewhere on the board
/CS_MAIN: SJ3.3; also elsewhere on the board
/DRDY: U4.47 (~DRDY); also elsewhere on the board
/PWDN: R8.2, U4.35 (~PWDN); also elsewhere on the board
AGND: C1.2, C2.2, C11.2, C13.2, C15.2, C17.2, C36.2, C39.2, R23.2, R24.2, R25.2, R26.2, SJ6.3, SJ7.3, U4.31 (RESV1), U4.33 (DGND), U4.38 (START), U4.49 (DGND), U4.51 (DGND), U4.60 (BIASREF); also elsewhere on the board
AIN1N: U4.15 (IN1N); also elsewhere on the board
AIN1P: U4.16 (IN1P); also elsewhere on the board
AIN2N: U4.13 (IN2N); also elsewhere on the board
AIN2P: U4.14 (IN2P); also elsewhere on the board
AIN3P: U4.12 (IN3P); also elsewhere on the board
AIN4P: U4.10 (IN4P); also elsewhere on the board
AIN5P: U4.8 (IN5P); also elsewhere on the board
AIN6P: U4.6 (IN6P); also elsewhere on the board
AIN7P: U4.4 (IN7P); also elsewhere on the board
AIN8P: U4.2 (IN8P); also elsewhere on the board
BIAS: C3.2, R9.1, SJ5.2, U3.3 (+IN_A), U4.62 (BIASIN), U4.63 (BIASOUT); also elsewhere on the board
CLK: P4.1, P5.2, U4.37 (CLK)
DAISY_OUT: P5.1, SJ4.1
MISO: SJ4.3; also elsewhere on the board
MOSI: U4.34 (DIN); also elsewhere on the board
unnamed: R23.1, U4.42 (GPIO1)
unnamed: R24.1, U4.44 (GPIO2)
unnamed: R25.1, U4.45 (GPIO3)
unnamed: R26.1, U4.46 (GPIO4)
REF_IN: P4.4, P5.3, U3.5 (+IN_B); also elsewhere on the board
SCLK: U4.40 (SCLK); also elsewhere on the board
SHIELD: U3.1 (OUT_A), U3.2 (-IN_A); also elsewhere on the board

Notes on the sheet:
For daisy-chain operation, use the following jumper settings: SJ1, SJ2, SJ6, SJ7 @ 2-3 for master AFE (provides clock and bias supply); SJ1, SJ2, SJ6, SJ7 @ 1-2 for additional AFEs

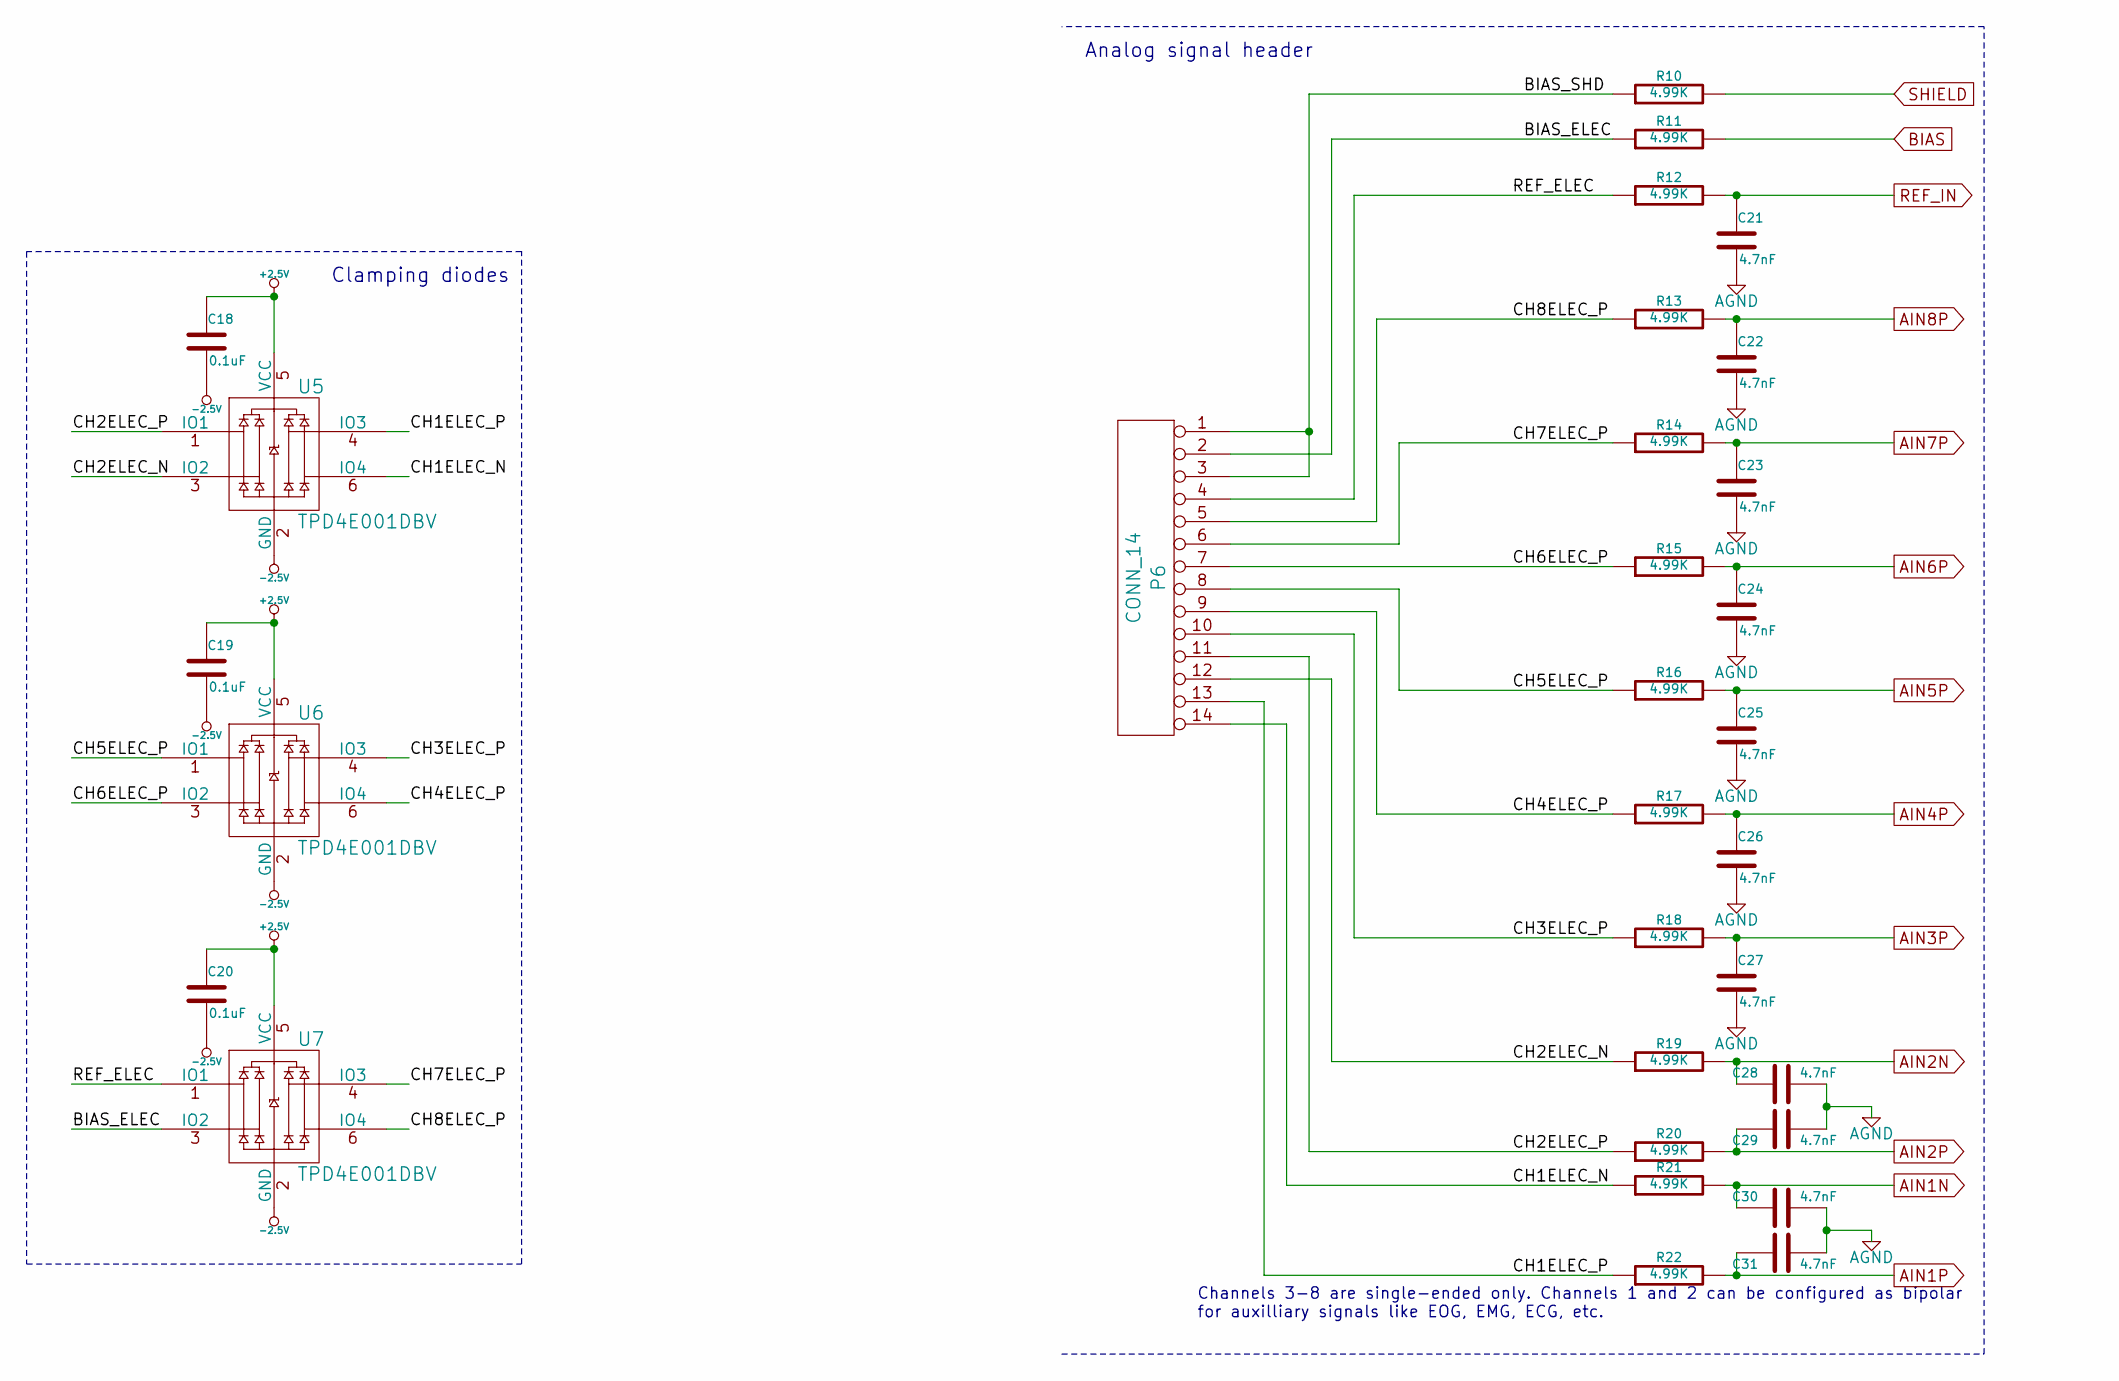
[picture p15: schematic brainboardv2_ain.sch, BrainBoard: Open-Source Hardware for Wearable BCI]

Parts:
C18, C19, C20: 0.1uF
C21, C22, C23, C24, C25, C26, C27, C28, C29, C30, C31: 4.7nF
P6: CONN_14
R10, R11, R12, R13, R14, R15, R16, R17, R18, R19, R20, R21, R22: 4.99K
U5, U6, U7: TPD4E001DBV

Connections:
+2.5V: C18.1, C19.1, C20.1, U5.5 (VCC), U6.5 (VCC), U7.5 (VCC); also elsewhere on the board
-2.5V: C18.2, C19.2, C20.2, U5.2 (GND), U6.2 (GND), U7.2 (GND); also elsewhere on the board
/Brainboard Analog In/BIAS_ELEC: P6.2, R11.1, U7.3 (IO2)
/Brainboard Analog In/BIAS_SHD: P6.1, P6.3, R10.1
/Brainboard Analog In/CH1ELEC_N: P6.14, R21.1, U5.6 (IO4)
/Brainboard Analog In/CH1ELEC_P: P6.13, R22.1, U5.4 (IO3)
/Brainboard Analog In/CH2ELEC_N: P6.12, R19.1, U5.3 (IO2)
/Brainboard Analog In/CH2ELEC_P: P6.11, R20.1, U5.1 (IO1)
/Brainboard Analog In/CH3ELEC_P: P6.10, R18.1, U6.4 (IO3)
/Brainboard Analog In/CH4ELEC_P: P6.9, R17.1, U6.6 (IO4)
/Brainboard Analog In/CH5ELEC_P: P6.8, R16.1, U6.1 (IO1)
/Brainboard Analog In/CH6ELEC_P: P6.7, R15.1, U6.3 (IO2)
/Brainboard Analog In/CH7ELEC_P: P6.6, R14.1, U7.4 (IO3)
/Brainboard Analog In/CH8ELEC_P: P6.5, R13.1, U7.6 (IO4)
/Brainboard Analog In/REF_ELEC: P6.4, R12.1, U7.1 (IO1)
AGND: C21.2, C22.2, C23.2, C24.2, C25.2, C26.2, C27.2, C28.2, C29.2, C30.2, C31.2; also elsewhere on the board
AIN1N: C30.1, R21.2; also elsewhere on the board
AIN1P: C31.1, R22.2; also elsewhere on the board
AIN2N: C28.1, R19.2; also elsewhere on the board
AIN2P: C29.1, R20.2; also elsewhere on the board
AIN3P: C27.1, R18.2; also elsewhere on the board
AIN4P: C26.1, R17.2; also elsewhere on the board
AIN5P: C25.1, R16.2; also elsewhere on the board
AIN6P: C24.1, R15.2; also elsewhere on the board
AIN7P: C23.1, R14.2; also elsewhere on the board
AIN8P: C22.1, R13.2; also elsewhere on the board
BIAS: R11.2; also elsewhere on the board
REF_IN: C21.1, R12.2; also elsewhere on the board
SHIELD: R10.2; also elsewhere on the board

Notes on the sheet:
Clamping diodes
Analog signal header
Channels 3-8 are single-ended only. Channels 1 and 2 can be configured as bipolar for auxilliary signals like EOG, EMG, ECG, etc.


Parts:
C32, C33: 0.1uF
C34: 2.2nF
C35: 0.01uF
U8: MPU6050

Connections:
+3.3V: C32.1, C35.1, U8.8 (VLOGIC), U8.13 (VDD); also elsewhere on the board
/Brainboard IMU/CPOUT: C34.1, U8.20 (CPOUT)
/Brainboard IMU/REGOUT: C33.1, U8.10 (REGOUT)
AGND: C32.2, C33.2, C34.2, C35.2, U8.1 (CLKIN), U8.9 (AD0), U8.11 (FSYNC), U8.18 (GND); also elsewhere on the board
I2C2_SCL: U8.23 (SCL); also elsewhere on the board
I2C2_SDA: U8.24 (SDA); also elsewhere on the board
IMU_INT: U8.12 (INT); also elsewhere on the board

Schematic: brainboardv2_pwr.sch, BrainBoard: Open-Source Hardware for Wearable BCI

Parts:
C37, C38, C40, C41: 1uF
C43, C44: 0.01uF
C45, C46: 10uF
C47, C48: 2.2uF
C49: 0.1uF
D1: LED
P7: -3V3
P8: +2V5
P9: -2V5
R27: 330
S2: DPDT
U9: TPS60403
U10: TPS73225
U11: TPS72325

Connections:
+2.5V: C45.1, C47.1, C49.1, P8.1, U10.5; also elsewhere on the board
+3.3V: C37.1, C41.1, D1.1 (A), S2.2, S2.5, U9.2 (IN), U10.1, U10.3; also elsewhere on the board
-2.5V: C46.1, C48.1, C49.2, P9.1, U11.5 (OUT); also elsewhere on the board
-3.3V: C40.1, P7.1, U9.1 (OUT), U11.2 (IN), U11.3 (EN)
AGND: C37.2, C40.2, C41.2, C43.2, C44.2, C45.2, C46.2, C47.2, C48.2, R27.2, U9.4 (GND), U10.2, U11.1 (GND); also elsewhere on the board
unnamed: C44.1, U11.4 (NR)
unnamed: C43.1, U10.4
unnamed: D1.2 (K), R27.1
unnamed: C38.1, U9.5 (CFLY+)
unnamed: C38.2, U9.3 (CFLY-)
VCC: S2.1, S2.4; also elsewhere on the board


Board: 4 copper layers, 86.4 x 54.6 mm, 105 parts (0 on the bottom side), 72 nets.

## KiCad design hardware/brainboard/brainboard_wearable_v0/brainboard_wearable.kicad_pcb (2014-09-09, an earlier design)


Board: 4 copper layers, 40.0 x 50.8 mm, 59 parts (0 on the bottom side), 48 nets.

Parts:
BT1: LIR2450; keystone_3008
C1, C2, C4, C5, C6, C13, C14, C19, C27, C29: 0.1uF; c_0402
C3, C11, C23, C24, C26, C28: 1uF; c_0402
C7, C8: 30pF; c_0402
C9, C10, C12, C20: 10uF; c_0603
C21, C22: 4.7nF; c_0402
C25: 1.5nF; c_0402
D1: RED; Led_0402
FB1: BLM18PG121SN1; inductor_smd_0603
L1: 10uH; inductor_smd_0603
MTG1: MHOLE; mounting_hole_0in125
P1: ICSP; pin_strip_3x2
P2: CONN_7X2; pin_socket_7x2-90
R1: 2.2M; r_0402
R2, R14: 1M; r_0402
R3, R4, R12, R13: 10k; r_0402
R6: 2.2k; r_0402
R11: 51k; r_0402
S1: JS102011SAQN
TP3: GND; testpoint_1mm
TP4: 3V3; testpoint_1mm
TP10: BTRX; PINTST
TP11: BTTX; PINTST
TP12: BTRTS; PINTST
TP13: BTCTS; PINTST
TP14: CONN; testpoint_1mm
TP16: FACT; testpoint_1mm
TP17: STATUS; PINTST
U1: FR015L3EZ; MLP6-2x2
U2: TPS727XXDSE; S-PWSON-N6
U3: ATMEGA328P-28PIN; qfn-28-nopad
U4: ADXL362; 16-LGA-3x3.25
U5: BLUETOOTH-RN42; roving_rn-42
U6: OPA376; sc70-5
U7: ADS1291/2; s-pvqfn-n32-nopad
Y1: ABM3B-8.000MHZ; crystal_smd_5x3.2mm

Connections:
+BATT: BT1.1, C9.1, C10.1, R1.1, S1.1, U1.3
/AREF: C4.1, U3.17
/AVCC: C2.1, L1.1, U3.16
/B-: BT1.2, U1.1, U1.2, U1.5, U1.6
/BATT_MON: C5.1, R1.2, R2.1, U3.9
/BT_CONN: TP14.1, U3.21, U5.19
/BT_RESET: U3.20, U5.5
/Electrode front-end/GPIO1: R12.1, U7.26
/Electrode front-end/GPIO2: R13.1, U7.25
/Electrode front-end/PGA1N: C21.2, U7.1
/Electrode front-end/PGA1P: C21.1, U7.2
/Electrode front-end/PGA2N: C22.2, U7.7
/Electrode front-end/PGA2P: C22.1, U7.8
/Electrode front-end/RLDIN: C25.1, R11.1, R14.1, U6.1, U7.29, U7.30
/Electrode front-end/RLDINV: C25.2, R14.2, U7.28
/Electrode front-end/VCAP1: C24.1, U7.11
/Electrode front-end/VCAP2: C23.1, U7.27
/Electrode front-end/VREFP: C19.1, C20.1, U7.9
/FACTORY_RESET: TP16.1, U5.22
/STATUS: TP17.1, U5.21
/USER_LED: R6.2, U3.19
/~MCU_CTS: TP12.1, U3.1, U5.15
/~MCU_RTS: TP13.1, U3.2, U5.16
AVDD: C1.1, C26.1, C27.1, FB1.2, U6.5, U7.12, U7.31, U7.32
CH1N: P2.12, U7.3
CH1P: P2.11, U7.4
CH2N: P2.14, U7.5
CH2P: P2.13, U7.6
DVDD: C6.1, C11.1, C13.1, C14.1, C28.1, C29.1, FB1.1, L1.2, R3.1, TP4.1, U2.1, U3.3, U4.1, U4.14, U5.11, U7.23
GND: C1.2, C2.2, C3.2, C4.2, C5.2, C6.2, C7.1, C8.1, C9.2, C10.2, C11.2, C12.2, C13.2, C14.2, C19.2, C20.2, C23.2, C24.2, C26.2, C27.2, C28.2, C29.2, D1.2, MTG1.1, P1.6, R2.2, R4.1, R12.2, R13.2, TP3.1, U1.4, U2.3, U3.4, U3.18, U4.12, U4.13, U4.16, U5.1, U5.12, U5.28, U5.29, U6.2, U7.10, U7.13, U7.24
INT1: U3.22, U4.11
MCU_RX: TP11.1, U3.26, U5.14
MCU_TX: TP10.1, U3.27, U5.13
MISO: P1.1, U3.14, U4.7, U7.21
MOSI: P1.4, U3.13, U4.6, U7.19
unnamed: D1.1, R6.1
unnamed: C8.2, U3.6, Y1.2
unnamed: C7.2, U3.5, Y1.1
RLD: P2.2, R11.2
SCLK: P1.3, U3.15, U4.4, U7.20
SHIELD: P2.1, P2.3, U6.3, U6.4
VCC: C3.1, C12.1, S1.2, U2.4, U2.6
VEXT: P1.2, S1.3
~AFE_CS: U3.11, U7.18
~AFE_DRDY: U3.28, U7.22
~AFE_PWDN: R4.2, U3.7, U7.15
~MCU_RESET: P1.5, R3.2, U3.25
~XL_CS: U3.12, U4.8

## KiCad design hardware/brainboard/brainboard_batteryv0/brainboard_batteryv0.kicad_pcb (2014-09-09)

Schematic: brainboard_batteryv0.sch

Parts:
C1, C11: 0.1uF
C2, C3, C4, C5, C7: 10uF
C6, C8: 0.01uF
C9: 0.47uF
C10: 2.2uF
CON1: USB-MINI-B
D1: SMAJ7.0A
D2: PGOOD
D3: CHARGE
D4: PMEG2005AEA
D5: POWER
D6: ALRT
F1, F2: PTC 1.95A
P1: JST
P2: VBAT
P3: GND
P4: BBB_PMIC
P6: VBUS
P7: WP
P8: EN
P9: PREREG
P10: 3V3
R1: 75k
R2, R3, R4: 4.7k
R5, R17: 806k
R6: 191k
R7: 1.18k
R8, R10, R11, R18, R19: 2.2k
R9: 10k
R12, R13: 5.6k
R14: 30.1k
R15, R16: 52.3k
S1: SYSOFF
S2: BBB_SLEEP
SJ1, SJ2: BAT; SparkFun-Passives-SJ_2S-NO
SJ3: TS PMIC; SparkFun-Passives-SJ_2S
SJ4: A2-0; SparkFun-Passives-SJ_2S-NO
SJ5: A1-0; SparkFun-Passives-SJ_2S-NO
SJ6: LOWBAT_DIS; SparkFun-Passives-SJ_3_PASTE1&2
SJ7: SENSE; SparkFun-Passives-SJ_2S-NO
TH1: NTC 10K
U1: MAX17048
U2: BQ24074(T)
U3: 24C256
U4: TPS73601-SON
U5: LTC2951-1
U6: BEAGLEBONE_BLACK

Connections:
+3.3V: D4.2 (K), P10.1, R2.1, R3.1, R4.1, R9.1, R12.1, R13.1, R18.2, U3.8 (VCC), U6.A3 (VDD_3V3B), U6.A4 (VDD_3V3B), U6.B3 (VDD_3V3B), U6.B4 (VDD_3V3B)
+BATT: C1.1, C2.1, C3.1, F1.1, P2.1, R5.1, R17.1, SJ1.1, SJ2.1, SJ6.3, SJ7.1, U1.2 (CELL), U1.3 (VDD), U2.2 (BAT), U2.3 (BAT), U5.4 (VIN); also elsewhere on the board
/A0: R4.2, U3.1 (A0)
/A1: R3.2, SJ5.2, U3.2 (A1)
/A2: R2.2, SJ4.2, U3.3 (A2)
/B+: F1.2, P1.1
/BAT: P4.1, SJ1.2, SJ2.2
/BBB_TS: P4.2, R1.1, SJ3.1
/EN: P8.1, R17.2, U4.5, U5.7 (EN)
/FB: C8.2, R14.2, R15.2, U4.3
/ILIM: R7.2, U2.12 (ILIM)
/ISET: R8.1, U2.16 (ISET)
/LOWBAT: C6.1, R5.2, R6.1, SJ6.1
/OFFT: C9.1, U5.6 (OFFT)
/OUT: C7.1, C11.1, P9.1, R10.1, R11.1, R19.1, U2.5 (EN2), U2.10 (OUT), U2.11 (OUT), U4.8
/PWR_BUT: S2.1, S2.3, U6.B9 (PWR_BUT)
/REGOUT: C8.1, C10.1, D4.1 (A), R15.1, U4.1
/SCL: R13.2, U1.7 (SCL), U3.6 (SCL), U6.B19 (I2C2_SCL)
/SDA: R12.2, U1.8 (SDA), U3.5 (SDA), U6.B20 (I2C2_SDA)
/SENSE: P4.3, SJ7.2
/TMR: R16.1, U2.14 (TMR)
/TS: SJ3.2, TH1.1, U2.1 (TS)
/VBUS: C4.1, C5.1, D1.2 (K), F2.1, P6.1, U2.13 (IN)
/VIN: CON1.1 (VBUS), F2.2
/WP: P7.1, R9.2, U3.7 (WP)
/~ALRT: D6.2 (K), U1.5 (~ALRT)
/~CHG: D3.2 (K), U2.9 (~CHG)
/~KILL: SJ6.2, U5.5 (~KILL), U5.8 (~INT)
/~PB: S1.2, S1.4, U5.3 (~PB)
/~PGOOD: D2.2 (K), U2.7 (~PGOOD)
unnamed: D3.1 (A), R10.2
unnamed: D2.1 (A), R11.2
unnamed: D5.1 (A), R18.1
unnamed: D6.1 (A), R19.2

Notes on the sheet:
Fuel/gas gauge
Battery charger
3.3V regulation
BeagleBone Black battery connector included for experimentation; DO NOT COMBINE with on-board charger and LDO
EEPROM for cape config
Connect SENSE to BAT directly at battery terminal
TO DO: - Connection to ~ALRT~ on P8
Fast charging current = K_ISET/R_ISET K_ISET = [797..975], 890 typical R_ISET = 2.2k yields about 400mA, or 0.2C for 2000mAh cell Input current limit = K_ILIM/R_ILIM See datasheet for K_ILIM ranges R_ILIM = 1.18k yields 1.3A
Power-off logic
Undervoltage detection: ~KILL~ < 0.6V if VBATT < 3.1V, turning off regulator
Brief SYSOFF press latches EN hi-Z ("on"). Long (3 sec) press latches EN low ("off").
C_OFFT = (1.56e-4 uF/ms)*(t_offt - 33 ms) C_OFFT = 0.47 uF --> t_offt = 3.045 s
REGOUT = 1.204*(R17+R18)/R18
TPS73601 can supply up to 400mA w/ VDO = 70 mV @ 25 deg C
The 3.3V rail generated on-board is used when operating independently of the BeagleBone Black. D4 prevents reverse current in the event the BBB is accidentally used for power. REGOUT can be adjusted to compensate for voltage drop across D4, or D4 can be DNP and shorted.
DNP
T_MAXCHG = 10*K_TMR*R_TMR K_TMR = 48s/kOhm R_TMR = 52.3k gives about 7 hr safety cutoff
USB on bottom layer. DNP if using BBB's charging circuitry via 4-hole battery header.

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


Board: 2 copper layers, 86.4 x 54.6 mm, 65 parts (39 on the bottom side), 36 nets.

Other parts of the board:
Q1: SI2312; SOT23

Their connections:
+BATT: Q1.1; also elsewhere on the board

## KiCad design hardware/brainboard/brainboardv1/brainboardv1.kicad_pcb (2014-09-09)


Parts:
P1: WP
P5: GND
P7: 3V3
R1, R2, R3: 4.7K
R4: 10K
R5, R6: 5.6K
S2: SMT_BUTTON
SJ4: A2; SparkFun-Passives-SJ_2S-NOTRACE
SJ5: A1; SparkFun-Passives-SJ_2S-NOTRACE
U1: 24C256
U2: BEAGLEBONE_BLACK

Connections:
+3.3V: P7.1, R1.1, R2.1, R3.1, R4.1, R5.1, R6.1, U1.8 (VCC), U2.B3 (VDD_3V3B), U2.B4 (VDD_3V3B); also elsewhere on the board
/A0: R3.2, U1.1 (A0)
/A1: R2.2, SJ5.1, U1.2 (A1)
/A2: R1.2, SJ4.1, U1.3 (A2)
/CS_DAISY: U2.B42 (GPIO0_7); also elsewhere on the board
/CS_MAIN: U2.B28 (SPI1_CS0); also elsewhere on the board
/DRDY: U2.B25 (GPIO3_21); also elsewhere on the board
/PWDN: U2.A23 (MMC1_DAT4); also elsewhere on the board
/WP: P1.1, R4.2, U1.7 (WP)
AGND: P5.1, S2.1, S2.3, SJ4.2, SJ5.2, U1.4 (GND), U2.A1 (DGND), U2.A2 (DGND), U2.B1 (DGND), U2.B2 (DGND), U2.B34 (GNDA_ADC), U2.B43 (DGND), U2.B44 (DGND), U2.B45 (DGND), U2.B46 (DGND); also elsewhere on the board
CLK: U2.A25 (MMC1_DAT0); also elsewhere on the board
I2C2_SCL: R5.2, U1.6 (SCL), U2.B21 (MMC1_CLK); also elsewhere on the board
I2C2_SDA: R6.2, U1.5 (SDA), U2.B22 (UART2_RXD); also elsewhere on the board
MISO: U2.B30 (SPI1_D1); also elsewhere on the board
MOSI: U2.B29 (SPI1_D0); also elsewhere on the board
unnamed: S2.2, S2.4, U2.B9 (PWR_BUT)
SCLK: U2.B31 (SPI1_SCLK); also elsewhere on the board
UARTBT_CTS: U2.B20 (I2C2_SDA); also elsewhere on the board
UARTBT_RTS: U2.B19 (I2C2_SCL); also elsewhere on the board
UARTBT_RX: U2.B26 (UART1_RXD); also elsewhere on the board
UARTBT_TX: U2.B24 (UART1_TXD); also elsewhere on the board
UARTUC_RX: U2.B13 (UART4_TXD); also elsewhere on the board
UARTUC_TX: U2.B11 (UART4_RXD); also elsewhere on the board

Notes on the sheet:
I2C serial EEPROM for board ID
If using MCU for Bluetooth communications, make sure BBB UART1 RX/TX/RTS/CTS are configured as inputs to prevent bus contention!
UART2_TXD/RXD mux config to MODE2 (I2C2_SCL/SDA), I2C2_SCL/SDA mux config to MODE0 (UART1_RTSN/CTSN)
UARTBT on BBB UART1 (w/ HW flow control), UARTUC on BBB UART4 (no flow control)


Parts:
C17, C18, C19: 0.1uF
C20, C21, C22, C23, C24, C25, C26, C27, C28, C55, C56: 4.7nF
P2: CONN_14
R11, R12, R13, R14, R15, R16, R17, R18, R19, R20, R21, R22, R23: 4.99K
U5, U6, U7: TPD4E001DBV

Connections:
+2.5V: C17.1, C18.1, C19.1, U5.5 (VCC), U6.5 (VCC), U7.5 (VCC); also elsewhere on the board
-2.5V: C17.2, C18.2, C19.2, U5.2 (GND), U6.2 (GND), U7.2 (GND); also elsewhere on the board
/BrainBoard Analog In/BIAS_ELEC: P2.12, R12.1, U7.3 (IO2)
/BrainBoard Analog In/BIAS_SHD: P2.13, R11.1
/BrainBoard Analog In/CH1ELEC_N: P2.2, R22.1, U5.6 (IO4)
/BrainBoard Analog In/CH1ELEC_P: P2.1, R23.1, U5.4 (IO3)
/BrainBoard Analog In/CH2ELEC_N: P2.4, R20.1, U5.3 (IO2)
/BrainBoard Analog In/CH2ELEC_P: P2.3, R21.1, U5.1 (IO1)
/BrainBoard Analog In/CH3ELEC_P: P2.5, R19.1, U6.4 (IO3)
/BrainBoard Analog In/CH4ELEC_P: P2.6, R18.1, U6.6 (IO4)
/BrainBoard Analog In/CH5ELEC_P: P2.7, R17.1, U6.1 (IO1)
/BrainBoard Analog In/CH6ELEC_P: P2.8, R16.1, U6.3 (IO2)
/BrainBoard Analog In/CH7ELEC_P: P2.9, R15.1, U7.4 (IO3)
/BrainBoard Analog In/CH8ELEC_P: P2.10, R14.1, U7.6 (IO4)
/BrainBoard Analog In/REF_ELEC: P2.11, R13.1, U7.1 (IO1)
AGND: C20.2, C21.2, C22.2, C23.2, C24.2, C25.2, C26.2, C27.2, C28.2, C55.2, C56.2, P2.14; also elsewhere on the board
AIN1N: C28.1, R22.2; also elsewhere on the board
AIN1P: C56.1, R23.2; also elsewhere on the board
AIN2N: C27.1, R20.2; also elsewhere on the board
AIN2P: C55.1, R21.2; also elsewhere on the board
AIN3P: C26.1, R19.2; also elsewhere on the board
AIN4P: C25.1, R18.2; also elsewhere on the board
AIN5P: C24.1, R17.2; also elsewhere on the board
AIN6P: C23.1, R16.2; also elsewhere on the board
AIN7P: C22.1, R15.2; also elsewhere on the board
AIN8P: C21.1, R14.2; also elsewhere on the board
BIAS: R12.2; also elsewhere on the board
REF: C20.1, R13.2; also elsewhere on the board
SHIELD: R11.2; also elsewhere on the board

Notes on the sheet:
Clamping diodes
Analog signal header
Channels 3-8 are single-ended only. Channels 1 and 2 can be configured as bipolar for auxilliary signals like EOG, EMG, ECG, etc.


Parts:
C29, C31, C33, C34, C35: 0.1uF
C30: 2.2uF
C32: 10uF
P3: CONN_5X2
U8: ATUC3L064

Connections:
+3.3V: C29.1, C30.1, C31.1, C32.1, C33.1, C34.1, C35.1, P3.4, U8.17 (VDDIN), U8.18 (VDDCORE), U8.34 (ADVREFP), U8.35 (VDDANA), U8.42 (VDDIO), U8.48 (VDDIO); also elsewhere on the board
/BrainBoard MCU/RESET_MCU: P3.6, U8.22 (RESET_N)
/BrainBoard MCU/TCK: P3.1, U8.11 (PA00)
/BrainBoard MCU/TDI: P3.9, U8.4 (PA03)
/BrainBoard MCU/TDO: P3.3, U8.13 (PA02)
/BrainBoard MCU/TMS: P3.5, U8.14 (PA01)
/CS_DAISY: U8.3 (PA08); also elsewhere on the board
/CS_MAIN: U8.6 (PB00); also elsewhere on the board
/DRDY: U8.41 (PA18); also elsewhere on the board
/PWDN: U8.2 (PA09); also elsewhere on the board
AGND: C29.2, C30.2, C31.2, C32.2, C33.2, C34.2, C35.2, P3.2, P3.10, U8.1 (GND), U8.19 (GND), U8.33 (GNDANA), U8.43 (GND), U8.45 (GND); also elsewhere on the board
DAISY_OUT: P3.8; also elsewhere on the board
I2C2_SCL: U8.28 (PA04); also elsewhere on the board
I2C2_SDA: U8.12 (PA05); also elsewhere on the board
IMU_INT: U8.46 (PA10); also elsewhere on the board
MISO: U8.7 (PB02); also elsewhere on the board
MOSI: U8.8 (PB03); also elsewhere on the board
RESET_BT: U8.44 (PB11); also elsewhere on the board
SCLK: U8.16 (PB01); also elsewhere on the board
UARTBT_CTS: U8.29 (PB09); also elsewhere on the board
UARTBT_RTS: U8.32 (PB08); also elsewhere on the board
UARTBT_RX: U8.31 (PB07); also elsewhere on the board
UARTBT_TX: U8.30 (PB06); also elsewhere on the board
UARTUC_RX: U8.15 (PA07); also elsewhere on the board
UARTUC_TX: U8.10 (PA06); also elsewhere on the board

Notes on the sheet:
JTAG INTERFACE / TOP NON-PASS-THROUGH CONNECTOR
MCU uses on-chip oscillator to save board space.
/DRDY on EXTINT[5]


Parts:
D1: STAT
D2: CONN
P4: BTRST
R24, R25: 330
R26: 10K
U9: BLUETOOTH-RN42

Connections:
+3.3V: U9.11 (VDD); also elsewhere on the board
/BrainBoard Bluetooth/FACTORY: P4.1, R26.1, U9.22 (PIO4)
/BrainBoard Bluetooth/STATUS: D2.1 (A), U9.19 (PIO2)
/BrainBoard Bluetooth/STATUSn: D1.1 (A), U9.21 (PIO5)
AGND: R24.2, R25.2, R26.2, U9.1 (GND), U9.12 (GND1), U9.25 (GND2), U9.27 (GND3), U9.28 (GND4), U9.29 (GND5); also elsewhere on the board
unnamed: D2.2 (K), R25.1
unnamed: D1.2 (K), R24.1
RESET_BT: U9.5 (RESET); also elsewhere on the board
UARTBT_CTS: U9.15 (UARTRTS); also elsewhere on the board
UARTBT_RTS: U9.16 (UARTCTS); also elsewhere on the board
UARTBT_RX: U9.14 (UARTTX); also elsewhere on the board
UARTBT_TX: U9.13 (UARTRX); also elsewhere on the board


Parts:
C36, C39, C43, C48: 10uF
C37, C38, C40, C41, C46: 1uF
C42, C47: 0.01uF
C44, C49: 2.2uF
C45: 0.1uF
P6: -3V3
P8: +2V5
P9: -2V5
U10: TPS60403
U11: TPS73225
U12: TPS72325

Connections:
+2.5V: C43.1, C44.1, C45.1, P8.1, U11.5 (OUT); also elsewhere on the board
+3.3V: C36.1, C37.1, C41.1, U10.2 (IN), U11.1 (IN), U11.3 (EN); also elsewhere on the board
-2.5V: C45.2, C48.1, C49.1, P9.1, U12.5 (OUT); also elsewhere on the board
-3.3V: C39.1, C40.1, C46.1, P6.1, U10.1 (OUT), U12.2 (IN), U12.3 (EN)
AGND: C36.2, C37.2, C39.2, C40.2, C41.2, C42.2, C43.2, C44.2, C46.2, C47.2, C48.2, C49.2, U10.4 (GND), U11.2 (GND), U12.1 (GND); also elsewhere on the board
unnamed: C47.1, U12.4 (NR)
unnamed: C38.1, U10.5 (CFLY+)
unnamed: C38.2, U10.3 (CFLY-)
unnamed: C42.1, U11.4 (NR)


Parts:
C1, C6, C11, C12, C15, C16, C50: 0.1uF
C2: 1nF
C3: 10uF
C4, C5, C7, C9, C10, C13, C14: 1uF
C8: 100uF
P10: CONN_2X2
R7, R8: 10K
R9: 499K,0.1%
SJ1: REF-SRB2; SparkFun-Passives-SJ_3_PASTE2&3
SJ2, SJ7: DAISY_CS; SparkFun-Passives-SJ_3_PASTE2&3
SJ3: NO BIAS FILT; SparkFun-Passives-SJ_2S-NO
SJ6: DAISY_OUT; SparkFun-Passives-SJ_3_PASTE2&3
SJ8: CLKSEL; SparkFun-Passives-SJ_3_PASTE1&2
U3: OPA2376; MSOP8
U4: ADS1299; TQFP_64

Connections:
+2.5V: C1.1, C9.1, C10.1, C11.1, C12.1, C13.1, C15.1, U3.8 (+V), U4.19 (AVDD), U4.21 (AVDD), U4.22 (AVDD), U4.54 (AVDD1), U4.56 (AVDD), U4.59 (AVDD); also elsewhere on the board
+3.3V: C14.1, C16.1, R7.1, R8.1, SJ8.1, U4.36 (~RESET), U4.48 (DVDD), U4.50 (DVDD); also elsewhere on the board
-2.5V: C3.1, C4.2, C5.2, C6.2, C7.2, C8.2, C9.2, C11.2, C13.2, C15.2, C50.1, U3.4 (-V), U4.20 (AVSS), U4.23 (AVSS), U4.25 (VREFN), U4.32 (AVSS), U4.53 (AVSS1), U4.57 (AVSS), U4.58 (AVSS); also elsewhere on the board
/BrainBoard AFE//CS: R7.2, SJ2.2, U4.39 (~CS)
/BrainBoard AFE/BIASINV: C2.1, R9.2, SJ3.1, U4.61 (BIASINV)
/BrainBoard AFE/CLKSEL: SJ8.2, U4.52 (CLKSEL)
/BrainBoard AFE/DAISY: SJ7.2, U4.41 (DAISY_IN)
/BrainBoard AFE/DAISY_IN: P10.1, SJ7.1
/BrainBoard AFE/DOUT: SJ6.2, U4.43 (DOUT)
/BrainBoard AFE/SRB1: U3.6 (-IN_B), U3.7 (OUT_B), U4.1 (IN8N), U4.3 (IN7N), U4.5 (IN6N), U4.7 (IN5N), U4.9 (IN4N), U4.11 (IN3N), U4.17 (SRB1)
/BrainBoard AFE/SRB2: SJ1.1, U4.18 (SRB2)
/BrainBoard AFE/VCAP1: C8.1, U4.28 (VCAP1)
/BrainBoard AFE/VCAP2: C7.1, U4.30 (VCAP2)
/BrainBoard AFE/VCAP3: C5.1, C6.1, U4.55 (VCAP3)
/BrainBoard AFE/VCAP4: C4.1, U4.26 (VCAP4)
/BrainBoard AFE/VREFP: C3.2, U4.24 (VREFP)
/CS_DAISY: SJ2.1; also elsewhere on the board
/CS_MAIN: SJ2.3; also elsewhere on the board
/DRDY: U4.47 (~DRDY); also elsewhere on the board
/PWDN: R8.2, U4.35 (~PWDN); also elsewhere on the board
AGND: C1.2, C10.2, C12.2, C14.2, C16.2, C50.2, SJ7.3, SJ8.3, U4.31 (RESV1), U4.33 (DGND), U4.38 (START), U4.42 (GPIO1), U4.44 (GPIO2), U4.45 (GPIO3), U4.46 (GPIO4), U4.49 (DGND), U4.51 (DGND); also elsewhere on the board
AIN1N: U4.15 (IN1N); also elsewhere on the board
AIN1P: U4.16 (IN1P); also elsewhere on the board
AIN2N: U4.13 (IN2N); also elsewhere on the board
AIN2P: U4.14 (IN2P); also elsewhere on the board
AIN3P: U4.12 (IN3P); also elsewhere on the board
AIN4P: U4.10 (IN4P); also elsewhere on the board
AIN5P: U4.8 (IN5P); also elsewhere on the board
AIN6P: U4.6 (IN6P); also elsewhere on the board
AIN7P: U4.4 (IN7P); also elsewhere on the board
AIN8P: U4.2 (IN8P); also elsewhere on the board
BIAS: C2.2, R9.1, SJ3.2, U3.3 (+IN_A), U4.62 (BIASIN), U4.63 (BIASOUT); also elsewhere on the board
CLK: U4.37 (CLK); also elsewhere on the board
DAISY_OUT: SJ6.1; also elsewhere on the board
MISO: SJ6.3; also elsewhere on the board
MOSI: U4.34 (DIN); also elsewhere on the board
unnamed: SJ1.2, U3.5 (+IN_B)
REF: SJ1.3; also elsewhere on the board
SCLK: U4.40 (SCLK); also elsewhere on the board
SHIELD: U3.1 (OUT_A), U3.2 (-IN_A); also elsewhere on the board

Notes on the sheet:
For daisy-chain operation, use the following jumper settings: SJ2, SJ6, SJ7, SJ8 @ 2-3 for master AFE (provides clock and bias supply); SJ2, SJ6, SJ7, SJ8 @ 1-2 for additional AFEs


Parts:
C51, C52: 0.1uF
C53: 2.2nF
C54: 0.01uF
SJ9: I2C Address Select (2&3NC); SparkFun-Passives-SJ_3_PASTE2&3
U13: MPU6050

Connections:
+3.3V: C51.1, C54.1, SJ9.1, U13.8 (VLOGIC), U13.13 (VDD); also elsewhere on the board
/BrainBoard IMU/AD0: SJ9.2, U13.9 (AD0)
/BrainBoard IMU/CPOUT: C53.1, U13.20 (CPOUT)
/BrainBoard IMU/REGOUT: C52.1, U13.10 (REGOUT)
AGND: C51.2, C52.2, C53.2, C54.2, SJ9.3, U13.1 (CLKIN), U13.11 (FSYNC), U13.18 (GND); also elsewhere on the board
I2C2_SCL: U13.23 (SCL); also elsewhere on the board
I2C2_SDA: U13.24 (SDA); also elsewhere on the board
IMU_INT: U13.12 (INT); also elsewhere on the board


Board: 4 copper layers, 86.4 x 54.6 mm, 116 parts (0 on the bottom side), 86 nets.

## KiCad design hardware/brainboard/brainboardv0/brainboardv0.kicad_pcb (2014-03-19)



Board: 4 copper layers, 86.4 x 54.6 mm, 86 parts (16 on the bottom side), 70 nets.

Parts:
C1, C6, C11, C12, C15, C16, C17, C18, C19, C29, C31, C33, C34, C35, C36: 0.1uF; SM0603
C2: 1nF; SM0603
C3, C32: 10uF; SM0805
C4, C5, C7, C9, C10, C13, C14: 1uF; SM0603
C8: 100uF; SM1206
C20, C21, C22, C23, C24, C25, C26, C27, C28: 4.7nF; SM0603
C30: 2.2uF; SM0603
D1: RED; LED-0603
D2: GREEN; LED-0603
P1: WP; PINTST
P2: CONN_12; PIN_ARRAY-12X1
P3: CONN_5X2; PIN_ARRAY_5x2
P4: BTRST; PINTST
P5: GND; PINTST
P6: 5VD; PINTST
P7: 3V3; PINTST
P8: 5VA; PINTST
R1, R2, R3: 4.7K; SM0603
R4, R7, R8, R10, R24: 10K; SM0603
R5, R6: 5.6K; SM0603
R9: 499K,0.1%; SM0805
R11, R12, R13, R14, R15, R16, R17, R18, R19, R20, R21: 4.99K; SM0603
R22, R23: 330; SM0603
S2: SMT_BUTTON; KMR231GLFS
SJ1, SJ2: SOLDERJUMPER_2WAYPASTE2&3; SparkFun-Passives-SJ_3_PASTE2&3
SJ3: SOLDERJUMPERNO; SparkFun-Passives-SJ_2S-NO
SJ4, SJ5: SOLDERJUMPERNC2; SparkFun-Passives-SJ_2S-NOTRACE
U1: 24C256; SSOP8
U2: BEAGLEBONE_BLACK
U3: OPA2376; MSOP_8
U4: ADS1299; TQFP_64
U5, U6, U7: TPD4E001; SOT23_6
U8: ATUC3L064; -TQFP48
U9: BLUETOOTH-RN42; SparkFun-RF-RN41
U10: TPS73150; SOT23-5

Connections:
3V3: C14.1, C16.1, C29.1, C30.1, C31.1, C32.1, C33.1, C34.1, C35.1, P3.4, P7.1, R1.1, R2.1, R3.1, R4.1, R5.1, R6.1, R7.1, R8.1, R10.1, U1.8, U2.B3, U2.B4, U4.48, U4.50, U4.52, U8.17, U8.18, U8.34, U8.35, U8.42, U8.48, U9.11
+5VA: C1.1, C9.1, C10.1, C11.1, C12.1, C13.1, C15.1, C17.1, C18.1, C19.1, P8.1, U3.8, U4.19, U4.21, U4.22, U4.54, U4.56, U4.59, U5.6, U6.6, U7.6, U10.5
+5VD: P6.1, U2.B7, U2.B8, U10.1, U10.3
/A0: R3.2, U1.1
/A1: R2.2, SJ5.1, U1.2
/A2: R1.2, SJ4.1, U1.3
/BrainBoard AFE/BIASIN: SJ2.1, U4.62
/BrainBoard AFE/BIASINV: C2.1, R9.2, U4.61
/BrainBoard AFE/BIASOUT: C2.2, R9.1, SJ3.2, U4.63
/BrainBoard AFE/SRB1: U3.6, U3.7, U4.17
/BrainBoard AFE/SRB2: SJ1.1, U4.18
/BrainBoard AFE/VCAP1: C8.1, U4.28
/BrainBoard AFE/VCAP2: C7.1, U4.30
/BrainBoard AFE/VCAP3: C5.1, C6.1, U4.55
/BrainBoard AFE/VCAP4: C4.1, U4.26
/BrainBoard AFE/VREFP: C3.2, U4.24
/BrainBoard Analog In/BIAS_ELEC: P2.10, R12.1, U7.2
/BrainBoard Analog In/BIAS_SHD: P2.9, R13.1, U7.4
/BrainBoard Analog In/CH1ELEC_P: P2.1, R21.1, U5.4
/BrainBoard Analog In/CH2ELEC_P: P2.2, R20.1, U5.5
/BrainBoard Analog In/CH3ELEC_P: P2.3, R19.1, U5.1
/BrainBoard Analog In/CH4ELEC_P: P2.4, R18.1, U5.2
/BrainBoard Analog In/CH5ELEC_P: P2.5, R17.1, U6.4
/BrainBoard Analog In/CH6ELEC_P: P2.6, R16.1, U6.5
/BrainBoard Analog In/CH7ELEC_P: P2.7, R15.1, U6.1
/BrainBoard Analog In/CH8ELEC_P: P2.8, R14.1, U6.2
/BrainBoard Analog In/REF_ELEC: P2.11, R11.1, U7.1
/BrainBoard Bluetooth/FACTORY: P4.1, R24.1, U9.22
/BrainBoard Bluetooth/STATUS: D2.1, U9.19
/BrainBoard Bluetooth/STATUSn: D1.1, U9.21
/BrainBoard MCU/RESET_MCU: P3.6, U8.22
/BrainBoard MCU/TCK: P3.1, U8.11
/BrainBoard MCU/TDI: P3.9, U8.4
/BrainBoard MCU/TDO: P3.3, U8.13
/BrainBoard MCU/TMS: P3.5, U8.14
/CS: R7.2, U4.39, U8.6
/DRDY: U4.47, U8.31
/PWDN: R8.2, U4.35, U8.25
/RESET: R10.2, U4.36, U8.21
/SCL: R5.2, U1.6, U2.B19
/SDA: R6.2, U1.5, U2.B20
/WP: P1.1, R4.2, U1.7
AGND: C1.2, C3.1, C4.2, C5.2, C6.2, C7.2, C8.2, C9.2, C10.2, C11.2, C12.2, C13.2, C14.2, C15.2, C16.2, C17.2, C18.2, C19.2, C20.2, C21.2, C22.2, C23.2, C24.2, C25.2, C26.2, C27.2, C28.2, C29.2, C30.2, C31.2, C32.2, C33.2, C34.2, C35.2, C36.2, P3.2, P3.10, P5.1, R22.2, R23.2, R24.2, S2.1, S2.3, SJ4.2, SJ5.2, U1.4, U2.A1, U2.A2, U2.B1, U2.B2, U2.B34, U2.B43, U2.B44, U2.B45, U2.B46, U3.4, U4.20, U4.23, U4.25, U4.31, U4.32, U4.33, U4.37, U4.49, U4.51, U4.53, U4.57, U4.58, U5.3, U6.3, U7.3, U8.1, U8.19, U8.33, U8.43, U8.45, U9.1, U9.12, U9.25, U9.27, U9.28, U9.29, U10.2
AIN1P: C28.1, R21.2, U4.16
AIN2P: C27.1, R20.2, U4.14
AIN3P: C26.1, R19.2, U4.12
AIN4P: C25.1, R18.2, U4.10
AIN5P: C24.1, R17.2, U4.8
AIN6P: C23.1, R16.2, U4.6
AIN7P: C22.1, R15.2, U4.4
AIN8P: C21.1, R14.2, U4.2
BIAS: R12.2, SJ2.3, U3.3
MISO: U4.43, U8.7
MOSI: U4.34, U8.8
unnamed: S2.2, S2.4, U2.B9
unnamed: SJ2.2, SJ3.1
unnamed: SJ1.2, U3.5
unnamed: D2.2, R23.1
unnamed: D1.2, R22.1
unnamed: C36.1, U10.4
REF: C20.1, R11.2, SJ1.3
RESET_BT: U8.30, U9.5
SCLK: U4.40, U8.16
SHIELD: R13.2, U3.1, U3.2
START: U4.38, U8.39
SYS_RESETn: U2.B10, U8.20
UARTBT_RX: U2.A37, U9.13
UARTBT_TX: U2.A38, U9.14
UARTUC_RX: U2.B13, U8.15
UARTUC_TX: U2.B11, U8.10

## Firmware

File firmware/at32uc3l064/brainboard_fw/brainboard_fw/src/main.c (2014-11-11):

/**
 *  \file main.c
 *
 *  \brief Brainboard setup and main loop.
 *  \author Graham Kelly
 *  \version 1.0
 *  \date August 2014
 *
 *  All Atmel Software Framework libraries used herein are copyright Atmel and 
 *  subject to their appropriate licenses, which allow free redistribution with
 *  some restrictions. These restrictions are listed in their appropriate files.
 *
 *  \page License
 *
 *  Brainboard firmware code is placed under the MIT license
 *  Copyright (c) 2014 Graham Kelly
 *
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
 */

#include <asf.h>
#include "brainboard.h"
#include "comms.h"
#include "ads1299.h"
#include "mpu60x0.h"				

#define FRAME_SIZE							128									// Size of each filtered segment (frame)
#define DSP_PREBUFFER_NB_SAMPLES			256									// # samples buffered between ADC and DSP engine
#ifndef FILT_COEFF_LENGTH
#define FILT_COEFF_LENGTH					65									
#endif
#define FILT_OUTPUT_SIZE					(FRAME_SIZE-FILT_COEFF_LENGTH+1)	// Size of filter output vector
#if ((FILT_OUTPUT_SIZE % 4) != 0)
#error Improper filter output buffer size										/* Must ensure FILT_OUTPUT_SIZE is divisible by 4
																				 * to meet Atmel's optimized DSP library specs
																				 */
#endif
	
/* BCI state machine */
/* Ultimately this should have more states for different paradigms */
typedef enum {
	DATA_STREAM = 0,
	MU_THRESHOLD = 1,
	MU_THRESHOLD_GYRO_MOUSE = 2
} processing_t;
processing_t processing_type;

/* Communication flags */
volatile uint32_t frame_complete_flag;

/* Communication counters and buffer management */
volatile uint32_t usart_tx_buffer_idx;
uint32_t spi_buf_write_idx, spi_buf_read_idx;

/* Buffers for data shuttling */
volatile uint8_t data_usart_rx_dma_buffer[3];
volatile uint32_t spi_rx_ads1299_status;
volatile int32_t spi_rx_data_buffer[DSP_PREBUFFER_NB_SAMPLES][MAX_EEG_CHANNELS];

/* Buffers for digital filtering: not currently implemented */
__attribute__((aligned(4))) dsp16_t dsp_filter_input_buffer[FRAME_SIZE];
__attribute__((aligned(4))) dsp16_t dsp_filter_output_buffer[FRAME_SIZE-FILT_COEFF_LENGTH+1];
/* Average value for mu frequency band: not currently implemented */
dsp32_t mu_band_avg;

int debug_usart;
spi_status_t debug_spi;


/* Data packet struct */
bboard_data24bit_packet_t data_usart_tx_packet =
{
	.start		= 0xA55A,
	.packetnum	= 0,
	.eegstatus  = {0, 0, 0},
	// .eegdata will be init with loop in main()
	// .imudata will be init with loop in main()
};

/* Mouse HID report for mouse mode */
mouse_hid_report_t report =
{
	.header		= 0xFD,
	.length		= 5,
	.descriptor = 2,
	.buttons	= 0x00,
	.dx			= 0,
	.dy			= 0,
	.wheel		= 0
};

/* Function prototypes */
void config_gpios(void);
void config_eic(void);
void config_dma(void);
void config_spi(void);
void config_usart(void);
status_code_t config_twim(void);
status_code_t config_rn42(volatile avr32_usart_t*);
status_code_t ads1299_check_device_id(uint8_t);

__attribute__((__interrupt__)) static void eic_handler(void)
{	
	Disable_global_interrupt();
	eic_clear_interrupt_line(&AVR32_EIC, ADS1299_DRDY_INT);
	
	if (processing_type == DATA_STREAM)
	/* If we're in data stream mode, there is no intermediate buffering, so write directly to USART TX packet */
	{
		/* Read back 24-bit status word and 8 channels of 24-bit data */
		ads1299_rdata24_packet(SPI_ADS1299_MAIN_CHIPNUM, usart_tx_buffer_idx, &data_usart_tx_packet);
		if (gpio_get_pin_value(MPU6050_INT_PIN))
		{
			/* Update inertial values Ax, Ay, Az, Gx, Gy, Gz */
			mpu6050_rdata16_packet(MPU6050_DEFAULT_ADDRESS, usart_tx_buffer_idx, &data_usart_tx_packet);
		}
		if (++usart_tx_buffer_idx == DATA_USART_TX_BUFFER_SIZE)
		{
			usart_tx_buffer_idx = 0;
			pdca_enable(DATA_USART_TX_PDCA_CHANNEL);
		}
	}
	else
	/* We have to pre-buffer the data for processing */
	{
		/* Read back 24-bit status word and 8 channels of 24-bit data; store in 32-bit ints */
		ads1299_rdata32_generic(SPI_ADS1299_MAIN_CHIPNUM, spi_buf_write_idx, spi_rx_ads1299_status, spi_rx_data_buffer);			
		if (gpio_get_pin_value(MPU6050_INT_PIN))
		{
			/* Update inertial values Ax, Ay, Az, Gx, Gy, Gz */
			mpu6050_rdata16_packet(MPU6050_DEFAULT_ADDRESS, usart_tx_buffer_idx, &data_usart_tx_packet);
		}			
		spi_buf_write_idx = (spi_buf_write_idx+1) % DSP_PREBUFFER_NB_SAMPLES;			
		if (spi_buf_write_idx % FRAME_SIZE == 0)
		{
			frame_complete_flag = 1;
		}
	}	
}

__attribute__((__interrupt__)) static void pdca_data_usart_tx_handler(void)
{
	pdca_disable(DATA_USART_TX_PDCA_CHANNEL);
	if (processing_type == DATA_STREAM)
	{
		pdca_load_channel(DATA_USART_TX_PDCA_CHANNEL, (void *)&data_usart_tx_packet, sizeof(data_usart_tx_packet));
		/* Circularly increment packet number */
		data_usart_tx_packet.packetnum = (data_usart_tx_packet.packetnum+1) % 128;
	}
	else
	{
		pdca_load_channel(DATA_USART_TX_PDCA_CHANNEL, (void *)&mu_band_avg, sizeof(mu_band_avg));
	}
}

__attribute__((__interrupt__)) static void pdca_data_usart_rx_handler(void)
{
	uint8_t readback;
	
	Disable_global_interrupt();
	
	DATA_USART->cr = AVR32_USART_CR_RTSDIS_MASK;
	
	/* To simplify DMA buffer implementation (i.e. to prevent me from having to code a timeout ISR
	 * when the user sends too few bytes to fill the buffer), multiple register reads/writes are not
	 * currently supported. For the sake of compatibility with the MATLAB command format of the previous
	 * implementation on Arduino, RREG and WREG commands are still 3 bytes long, but the second byte is
	 * ignored.
	 *
	 * !!!! For the following code to work, all commands MUST be 3 bytes long !!!!
	 */
	
	/* Code would go here to parse command switching between data streaming and frequency band extraction
	 * modes. Make sure value of this command is not included in set of ADS1299 commands.
	 */
	
	switch (data_usart_rx_dma_buffer[0] & 0xE0)
	{
		case 0x40:	// WREG
			ads1299_wreg(SPI_ADS1299_MAIN_CHIPNUM, data_usart_rx_dma_buffer[0] & 0x1F, data_usart_rx_dma_buffer[2]);
			break;
		case 0x20:	// RREG
			ads1299_rreg(SPI_ADS1299_MAIN_CHIPNUM, data_usart_rx_dma_buffer[0] & 0x1F, &readback);
			usart_putchar(DATA_USART, (int)readback);
			while(!usart_tx_empty(DATA_USART));
			break;
		default:
			ads1299_send_byte(SPI_ADS1299_MAIN_CHIPNUM, data_usart_rx_dma_buffer[0]);
			break;
	}
	if (data_usart_rx_dma_buffer[0] == ADS1299_OPC_STOP)
	{
		usart_tx_buffer_idx = 0;
		pdca_disable(DATA_USART_TX_PDCA_CHANNEL);
	}
	pdca_load_channel(DATA_USART_RX_PDCA_CHANNEL, (void *)data_usart_rx_dma_buffer, 3);
	DATA_USART->cr = AVR32_USART_CR_RTSEN_MASK;
	
	Enable_global_interrupt();
}

void config_dma(void)
{
	/* DMA configuration options for USART3 (RN-42 Bluetooth) data transmission.
	 * RN-42 is connected to USART3 on the UC3. The USART operates in byte mode, so transfer size must be BYTE.
	 */
	const pdca_channel_options_t pdca_data_usart_tx_opt = 
	{
		.pid			= DATA_USART_TX_PDCA_PID,
		.transfer_size	= PDCA_TRANSFER_SIZE_BYTE,
		.r_addr			= NULL,
		.r_size			= 0
	};
	
	/* DMA configuration options for USART3 (RN-42 Bluetooth) data receipt.
	 * RN-42 is connected to USART3 on the UC3. The USART operates in byte mode, so transfer size must be BYTE.
	 */
	const pdca_channel_options_t pdca_data_usart_rx_opt =
	{
		.pid			= DATA_USART_RX_PDCA_PID,
		.transfer_size	= PDCA_TRANSFER_SIZE_BYTE,
		.addr			= (void *)data_usart_rx_dma_buffer,
		.size			= 3,
		.r_addr			= NULL,
		.r_size			= 0
	};
	
	bool global_irq_enabled = cpu_irq_is_enabled();
	if (global_irq_enabled) {
		/* Turn off interrupts while we set stuff up */
		Disable_global_interrupt();
	}
	
	/* Init PDCA and register corresponding interrupts */
	/* USART3 receipt */
	pdca_init_channel(DATA_USART_RX_PDCA_CHANNEL, &pdca_data_usart_rx_opt);
	INTC_register_interrupt((__int_handler)&pdca_data_usart_rx_handler, AVR32_PDCA_IRQ_0 + DATA_USART_RX_PDCA_CHANNEL, AVR32_INTC_INT3);
	pdca_enable_interrupt_transfer_complete(DATA_USART_RX_PDCA_CHANNEL);
	
	/* USART3 transmission */
	pdca_init_channel(DATA_USART_TX_PDCA_CHANNEL, &pdca_data_usart_tx_opt);
	INTC_register_interrupt((__int_handler)&pdca_data_usart_tx_handler, AVR32_PDCA_IRQ_0 + DATA_USART_TX_PDCA_CHANNEL, AVR32_INTC_INT2);
	pdca_load_channel(DATA_USART_TX_PDCA_CHANNEL, (void *)&data_usart_tx_packet, sizeof(data_usart_tx_packet));
	pdca_enable_interrupt_transfer_complete(DATA_USART_TX_PDCA_CHANNEL);	
	
	if (global_irq_enabled) {
		/* Enable all interrupts */
		Enable_global_interrupt();
	}
}

void config_eic(void)
{

	const eic_options_t eic_drdy_opt =
	{
		.eic_mode    = EIC_MODE_EDGE_TRIGGERED,
		.eic_level   = EIC_EDGE_FALLING_EDGE,
		.eic_filter  = EIC_FILTER_DISABLED,
		.eic_async   = EIC_ASYNCH_MODE,
		.eic_line    = ADS1299_DRDY_INT
	};
	
	bool global_irq_enabled = cpu_irq_is_enabled();
	if (global_irq_enabled) {
		Disable_global_interrupt();
	}
	
	/* Register external DRDY interrupt */
	INTC_register_interrupt((__int_handler)&eic_handler, ADS1299_DRDY_IRQ, AVR32_INTC_INT0);
	eic_init(&AVR32_EIC, &eic_drdy_opt, 1);
	eic_enable_line(&AVR32_EIC, eic_drdy_opt.eic_line);
	eic_enable_interrupt_line(&AVR32_EIC, eic_drdy_opt.eic_line);
	
	if (global_irq_enabled) {
		Enable_global_interrupt();
	}
}

void config_spi(void)
{
	const spi_options_t spi_opt =
	{
		.reg			= SPI_ADS1299_MAIN_CHIPNUM,		// "Master" ADS1299 when daisy-chaining: connected to CS0
		.baudrate		= SPI_BAUDRATE,					// 1 MHz preferred baudrate
		.bits			= 8,							// 8 bits per character (range is 8 to 16)
		.spck_delay		= 0,							// Delay before first clock pulse after selecting slave (in PBA clock periods)
		.trans_delay	= 0,							// Delay between each transfer/character (in PBA clock periods)
		.stay_act		= true,							// Sets this chip to stay active after last transfer to it
		.spi_mode		= SPI_MODE_1,					// Which SPI mode to use (ADS1299 is mode 1)
		.modfdis		= true							// Disable the mode fault detection
	};
	
	/* Init SPI module as master */
	spi_initMaster(SPI_ADDRESS, &spi_opt);
	
	/* Setup configuration for chip connected to CS0 */
	debug_spi = spi_setupChipReg(SPI_ADDRESS, &spi_opt, sysclk_get_pba_hz());
	
	/* Allow the module to transfer data */
	spi_enable(SPI_ADDRESS);
}
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

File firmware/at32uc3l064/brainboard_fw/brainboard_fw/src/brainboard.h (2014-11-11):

/** 
 *  \file brainboard.h
 *  \brief Board-specific definitions for current Brainboard revision.
 *  \author Graham Kelly
 *  \version 1.0
 *  \date August 2014
 *
 *  All Atmel Software Framework libraries used herein are copyright Atmel and
 *  subject to their appropriate licenses, which allow free redistribution with
 *  some restrictions. These restrictions are listed in their appropriate files.
 *
 *  \page License
 *
 *  Brainboard firmware code is placed under the MIT license
 *  Copyright (c) 2014 Graham Kelly
 *
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
 */

#ifndef _BRAINBOARD_H_
#define _BRAINBOARD_H_

#include <compiler.h>

#define BRAINBOARD_REV					2	

//! \name Oscillator Definitions
// @{

/*! \brief System oscillator frequencies (Hz.) and startup times (periods).
 *
 * RCOsc has no custom calibration by default. Set the following definition
 * to the appropriate value if a custom RCOsc calibration has been applied
 * to your part.
 */

//!< RCOsc frequency: Hz.

#define FRCOSC                  (AVR32_SCIF_RCOSC_FREQUENCY)

//!< Osc32 frequency (Hz.) and startup time (RCOsc periods).

#define FOSC32                  (32768)
#define OSC32_STARTUP           (AVR32_SCIF_OSCCTRL32_STARTUP_131072_RCOSC)

#define BOARD_OSC32_IS_XTAL     true
#define BOARD_OSC32_HZ          FOSC32
#define BOARD_OSC32_STARTUP_US  (920000)
#define BOARD_OSC32_PINSEL      (0)


// The UC3-L0-Xplained does not have an Osc0 crystal.

#define FOSC0                   ((int) "NONE")
//#define OSC0_STARTUP          (AVR32_SCIF_OSCCTRL0_STARTUP_2048_RCOSC)

// @}

/* For the below values, clocks are derived from the uC's digital frequency-locked loop (DFLL),
 * divided by various clock dividers */
#define FCPU_HZ							(DFLL_FREQ_HZ >> CONFIG_SYSCLK_CPU_DIV) // CPU frequency in Hz
#define FPBA_HZ							(DFLL_FREQ_HZ >> CONFIG_SYSCLK_PBA_DIV) // Peripheral Bus A freq in Hz
#define FPBB_HZ							(DFLL_FREQ_HZ >> CONFIG_SYSCLK_PBB_DIV) // Peripheral Bus B freq in Hz

/*************************************************************************************************************************************************
 *               Host Pin Config Definitions                                                                                                     *
 *************************************************************************************************************************************************/

#if (BRAINBOARD_REV == 0)

/**
 *  \brief Defines the host processor pin assigned to the RESET pin on the ADS1299.
 */
#define ADS1299_PIN_RESET		AVR32_PIN_PB04

/**
 *  \brief Defines the host processor pin assigned to the START pin on the ADS1299.
 */
#define ADS1299_PIN_START		AVR32_PIN_PA17

#endif

/**
 *  \brief Defines the host processor pin assigned to the DRDY pin on the ADS1299.
 */
#define ADS1299_PIN_DRDY		AVR32_PIN_PA18
#define ADS1299_DRDY_INT		5
#define ADS1299_DRDY_PRIORITY	AVR32_INTC_INT3
#define ADS1299_DRDY_IRQ		AVR32_EIC_IRQ_5
#define ADS1299_DRDY_INT_FN		AVR32_EIC_EXTINT_5_0_FUNCTION	

/**
 *  \brief Defines the host processor pin assigned to the PWDN pin on the ADS1299.
 */
#define ADS1299_PIN_PWDN		AVR32_PIN_PA09	

/**
 *  \brief Defines the host processor pin assigned to the RESET pin on the RN-42.
 */
#define BT_RESET_PIN			AVR32_PIN_PB11

/**
 *  \brief Defines the host processor pin assigned to the INT pin on the MPU-6050.
 */
#if (BRAINBOARD_REV == 2)
#define MPU6050_INT_PIN			AVR32_PIN_PA07
#elif (BRAINBOARD_REV < 2)
#define MPU6050_INT_PIN			AVR32_PIN_PA10
#endif

#endif /* #ifndef _BRAINBOARD_H_ */

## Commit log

2013-07-24 Reorg w/ subdirectories for FW and HW
    [FlyingBone-Back.gbl, FlyingBone-Front.gtl, FlyingBone-Mask_Back.gbs, FlyingBone-Mask_Front.gts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]
2013-10-30 Added BB Rev 1 files
    Changelog: added missing traces on LEDs
    TODO: fix passives silkscreens too small or on top of pads, mark LED and
    tantalum polarities, enlarge P8 and P9 drills, mark TP vias on back
    silk, fix silk orientation consistency, break out SPI bus, try to place
    ADS1299 caps a bit closer to IC
    [brainboardv1.kicad_pcb, brainboardv1.sch, brainboardv1_afe.sch, brainboardv1_ain.sch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]
2013-12-27 Nearly finished v1 sch & brd, await final check
    Fixed errors from Rev 0, added MPU-6050 accelerometer/gyro for head
    motion tracking, switched to +/-2.5V analog supply, added 2 bipolar
    analog inputs for EOG tracking, added daisy-chain capability
    [brainboardv1.csv, brainboardv1.kicad_pcb, brainboardv1.sch, brainboardv1_afe.sch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]
2013-12-30 Added thicker power traces and fixed silkscreen
    [brainboardv1.kicad_pcb, brainboardv1.sch, brainboardv1_afe.sch, brainboardv1_ain.sch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]
2014-01-02 Added bottom layer ground plane
    [brainboardv1-B_Mask.gbs, brainboardv1-B_SilkS.gbo, brainboardv1-Bottom.gbl, brainboardv1-Edge_Cuts.gko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]
2014-01-02 Added cad for bottom layer ground plane
    [brainboardv1-B_Mask.gbs, brainboardv1-Bottom.gbl]
2014-01-02 Removed extra ground plane connection
    May not affect anything, especially on battery power, but trying to keep
    good layout practice
    [brainboardv1-Bottom.gbl, brainboardv1-Top.gtl, brainboardv1.kicad_pcb]
2014-01-03 Making dedicated battery board for now (rev0)
    Designed for Li-polymer batteries. Includes USB battery charging IC
    (MCP73831), footprints for 2 fuel gauges (pick one of MAX17043 or
    bq27510, because the former has an Arduino library but is impossible to
    source alone in small quantities), NTC thermistor, and 3.3V LDO.
    [brainboard_batteryv0.sch]
2014-01-03 Reorganized sch a bit
    [brainboard_batteryv0.sch]
2014-01-09 More battery changes
    Added power-down logic to battery board (currently faulty, need
    revision); added fuel gauge, 2-pin JST, and BBB battery connector to
    Brainboard R1.
    TODO: Fix power-down logic (suggest dedicated power-button supervisor
    like STM660x), add isolation so board can be safely plugged in to charge
    [brainboard_batteryv0.sch, brainboardv1.kicad_pcb, brainboardv1.sch, brainboardv1_afe.sch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]
2014-01-14 Just gonna use separate button for SYSOFF
    [brainboard_batteryv0.sch]
2014-01-29 Semi-finished battery board rev0
    Everything laid out and routed, still need to check alignment of BBB
    battery connector holes
    [brainboard_batteryv0.kicad_pcb, brainboard_batteryv0.sch, brainboard_batteryv0_BOM.ods]
2014-01-30 Finalized hole positions, gerbers/drills
    [brainboard_batteryv0-B_Cu.gbl, brainboard_batteryv0-B_Mask.gbs, brainboard_batteryv0-B_SilkS.gbo, brainboard_batteryv0-Edge_Cuts.gbr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]
2014-03-19 Organized, added wearable folder
    [FlyingBone-Back.gbl, FlyingBone-Front.gtl, FlyingBone-Mask_Back.gbs, FlyingBone-Mask_Front.gts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]
2014-09-09 Thesis version
    Finally able to commit again (Windows XP issues fixed by OS upgrade).
    Added latest version of wearable BB, along with prototype "muscleboard"
    2-channel board for EMG/ECG applications
    [brainboard_batteryv0-B_Cu.gbl, brainboard_batteryv0-B_Mask.gbs, brainboard_batteryv0-B_SilkS.gbo, brainboard_batteryv0-Edge_Cuts.gbr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]
2014-09-09 Thesis version redux
    Apparently some files didn't properly sync
    [$brainboard_wearable.sch, FlyingBone-Back.gbl, FlyingBone-Front.gtl, FlyingBone-Mask_Back.gbs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]
2014-10-15 BOM update
    [brainboard_wearable_v2.csv, muscleboardv0.csv, muscleboardv0_BOM.xlsx]
2014-10-22 Fixed CLKSEL and START no-connects on muscleboard
    Also removed extraneous components including battery voltage
    divider--going to use ATMEGA328p's internal voltage reference to measure
    AVCC instead. AVCC is now directly tied to VCC
    [muscleboardv0-B_Mask.gbs, muscleboardv0-B_Paste.gbp, muscleboardv0-B_SilkS.gbo, muscleboardv0-Bottom.gbl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]
2015-06-02 Fixing R1 BOM - still missing a few PNs/manufacturers
    Got rid of misnamed CSV files, removed non-physical "components" from
    ODT BOM
    TODO: Ensure all PNs/manufacturers are filled in, double-check for all
    BOMs
    [brainboardv1.csv, brainboardv1_BOM.csv, brainboardv1_BOM.ods]
2015-06-02 Fixed wearable_v2 BOM CSV
    May yet update all BOMs to a nicer spreadsheet format...
    [brainboard_wearable_v2.csv]
2015-06-12 Added missing PNs to BBv1 BOM
    [brainboardv1_BOM.ods]
2015-09-16 Regenerate R1 BOM
    [brainboardv1.csv, brainboardv1_BOM_REVISED.ods]
2015-09-16 Regenerated wearable_v2 BOM
    [brainboard_wearable_v2_BOM_REVISED.csv, brainboard_wearable_v2_BOM_REVISED.ods]
